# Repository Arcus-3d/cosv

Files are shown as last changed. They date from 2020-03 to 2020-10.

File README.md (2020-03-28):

## COSV - Cam Open Source Ventilator.
Cam based ventilator designed to fit directly on an BVM, on the patient.
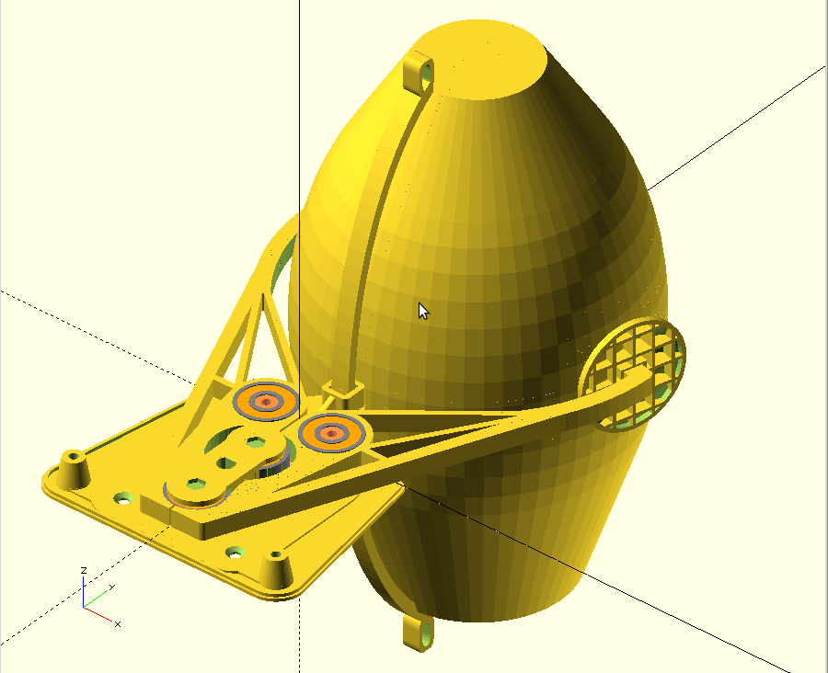
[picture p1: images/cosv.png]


The [COSV - Cam Open Source Ventilator](https://hackaday.io/project/170507) project is open source hardware. 
This github repository hosts the [OpenSCAD](http://www.openscad.org) source and the rendered STL images for quick access.

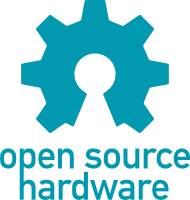
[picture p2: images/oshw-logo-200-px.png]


Hardware designs (schematics and CAD) files are licensed under the [Creative Commons Attribution-ShareAlike 3.0 Unported License](http://creativecommons.org/licenses/by-sa/3.0/) and follow the terms of the [OSHW (Open-source hardware) Statement of Principles 1.0.](http://freedomdefined.org/OSHW)

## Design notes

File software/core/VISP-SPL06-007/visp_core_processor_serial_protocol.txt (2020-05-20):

VISP Core Processor Serial Data Format

Note: <t> is time on the core,based on milliseconds since power up.

Sensor Readings
d,<t>,<pressure cmH20>,<smoothed volume (mL)>,<tidal volume (mL)>[,<s1>,<s2>,<s3>,<s4>] (UNSOLICITED)

Logging Output (UNSOLICITED)
i,<t>,<informational string>
g,<t>,<debug string>
w,<t>,<warning string>
c,<t>,<critical string>

Health Status Reports have the text "good" or "bad" based on the active status of the core. (can be UNSOLICITED)
H

Core responds with timestamp and status string.
H,<t>,[good|bad]

Calibrate now
C
Core responds with timestamp, status code, and status string.
C,<t>,<status>,<string>

Example responses:
C,<t>,0,Starting
C,<t>,1,In Progress
C,<t>,2,Complete

Reboot command.   Reboots the core
R
Core does not respond to a Reboot command

Identification Command (UNSOLICITED RESPONSE HAPPENS AT STARTUP)
I
Core responds with
I,<t>,<string>,<major>,<minor>,<revision>

EEPROM read/write
An empty parameter string makes the core echo back all 128 bytes of EEPROM data.
Providing the address will reply with a full page (16-bytes) starting at that address,
Providing the address and data will write the data to the EEPROM, on write
to byte 127, the EEPROM data will be committed to the EEPROM.
E
E,<address>
E,<address>,<b_0>

Response will always consist of a time, address, and data bytes
E,<t>,<address>,<b0>,<b1>,<b2>...

Settings.  There are many settings available, use 'Q' to query them all
S
Core replies with all settings (no limits or dictionaries)

Example S output
S,176825,mode,value,PC-CMV
S,176825,rate,value,5
S,176826,ie,value,1:2
S,176826,volume,value,0
S,176828,pressure,value,0
S,176830,breathThreshold,value,0
S,176833,bodytype,value,Venturi
S,176836,calib0,value,-38256.90
S,176838,calib1,value,-38303.29
S,176841,calib2,value,-37957.33
S,176844,calib3,value,114517.55
S,176847,sensor0,value,BMP280
S,176849,sensor1,value,BMP280
S,176852,sensor2,value,BMP388
S,176855,sensor3,value,BMP388
S,176858,motorType,value,Unknown
S,176861,motorSpeed,value,0
S,176863,motorMinSpeed,value,60
S,176866,motorHomingSpeed,value,0
S,176869,motorStepsPerRev,value,200
S,176872,debug,value,Disable

Settings Query 1 setting command
S,mode
Core replies with the current "mode" setting
S,<t>,mode,Unknown

Settings set command
S,mode,PC-CMV
Core replies with the current setting with a list of *_display Enabled/Disabled for the settings relavent to this mode
S,<t>,mode,PC-CMV

Example "S,mode,PC-CMV" output
S,140581,mode,value,PC-CMV
S,140581,mode,enabled,True
S,140582,rate,enabled,True
S,140583,ie,enabled,True
S,140585,volume,enabled,False
S,140588,pressure,enabled,True
S,140591,breathThreshold,enabled,False
S,140594,bodytype,enabled,False
S,140597,calib0,enabled,False
S,140600,calib1,enabled,False
S,140602,calib2,enabled,False
S,140605,calib3,enabled,False
S,140607,sensor0,enabled,False
S,140610,sensor1,enabled,False
S,140613,sensor2,enabled,False
S,140615,sensor3,enabled,False
S,140618,motorType,enabled,True
S,140621,motorSpeed,enabled,True
S,140624,motorMinSpeed,enabled,True
S,140627,motorHomingSpeed,enabled,True
S,140631,motorStepsPerRev,enabled,True
S,140634,debug,enabled,True

mode sets the operational mode using "PC-CMV" or "VC-CMV)
rate controls the rate in which the breath is delivered
volume controls the volume in mL of breaths (tidal volume)
pressure controls the pressure used in PC-CMV
ie is the inhale:exhale ratio
breathInterval controls the time period between breaths in milliseconds. (Continuous Mandatory Ventilation)
debug enable or disable the internal debugging output
motorSpeed Internal testing, turns motor on at a specific speed
bodytype Switches the algorithm used for the core
calib0-3 Current calibration settings for each sensor
sensor0-3 Current sensor detected.  Sensor0=U5, Sensor1=U6, Sensor2=U7, Sensor3=U8
motorType Used to set the type of motor attached 
motorSpeed Used to set the current speed of the motor
motorMinSpeed Minimum speed for the motor to use for initial starting of a breath cycle
motorHomingSpeed Homing speed of the motor
motorStepsPerRev For steppers, how many steps per rev (200, 400, etc)

Query all settings.  This a display will want to do on startup, to determine the capabilities of the core.
Q
The Core will respond with 'H', and 'S' responses for all settings and limits/dictionaries.

Example Q output
S,2394,mode,dict,OFF,Offline,PC-CMV,Pressure Controlled CMV,VC-CMV,Volume Controlled CMV
S,2397,mode,group,button
S,2399,mode,enabled,True
S,2401,mode,value,OFF
S,2403,rate,min,5
S,2405,rate,max,20
S,2406,rate,group,button
S,2409,rate,enabled,True
S,2411,rate,value,5
S,2413,ie,dict,1:2,50% duty cycle,1:3,33% duty cycle,1:4,25% duty cycle,1:5,20% duty cycle
S,2420,ie,group,button
S,2422,ie,enabled,True
S,2424,ie,value,1:2
S,2426,volume,min,0
S,2428,volume,max,1000
S,2430,volume,group,button
S,2433,volume,units,mL
S,2435,volume,enabled,True
S,2437,volume,value,0
S,2439,pressure,min,0
S,2441,pressure,max,100
S,2443,pressure,group,button
S,2446,pressure,units,cmH2O
S,2448,pressure,enabled,True
S,2451,pressure,value,0
S,2453,breathThreshold,min,0
S,2455,breathThreshold,max,1000
S,2458,breathThreshold,group,button
S,2461,breathThreshold,enabled,False
S,2464,breathThreshold,value,0
S,2467,bodytype,dict,Unknown,Unknown,Pitot,Pitot body style,Venturi,Venturi body style
S,2475,bodytype,group,button
S,2478,bodytype,enabled,False
S,2480,bodytype,value,Venturi
S,2483,calib0,min,-1000
S,2485,calib0,max,1000
S,2487,calib0,group,status
S,2489,calib0,units,pascals
S,2491,calib0,enabled,False
S,2494,calib0,value,5035907.00
S,2497,calib1,min,-1000
S,2499,calib1,max,1000
S,2501,calib1,group,status
S,2503,calib1,units,pascals
S,2505,calib1,enabled,False
S,2508,calib1,value,5038159.00
S,2510,calib2,min,-1000
S,2512,calib2,max,1000
S,2514,calib2,group,status
S,2518,calib2,units,pascals
S,2520,calib2,enabled,False
S,2523,calib2,value,5021042.50
S,2525,calib3,min,-1000
S,2527,calib3,max,1000
S,2529,calib3,group,status
S,2532,calib3,units,pascals
S,2534,calib3,enabled,False
S,2536,calib3,value,-2525668.30
S,2539,sensor0,dict,Unknown,Unknown,BMP388,BMP388,BMP280,BMP280,SPL06,SPL06
S,2546,sensor0,group,status
S,2548,sensor0,enabled,False
S,2550,sensor0,value,BMP280
S,2553,sensor1,dict,Unknown,Unknown,BMP388,BMP388,BMP280,BMP280,SPL06,SPL06
S,2560,sensor1,group,status
S,2563,sensor1,enabled,False
S,2565,sensor1,value,BMP280
S,2568,sensor2,dict,Unknown,Unknown,BMP388,BMP388,BMP280,BMP280,SPL06,SPL06
S,2574,sensor2,group,status
S,2576,sensor2,enabled,False
S,2579,sensor2,value,BMP388
S,2581,sensor3,dict,Unknown,Unknown,BMP388,BMP388,BMP280,BMP280,SPL06,SPL06
S,2588,sensor3,group,status
S,2590,sensor3,enabled,False
S,2593,sensor3,value,BMP388
S,2595,motorType,dict,Unknown,Unknown,AutoDetect,Start Motor Autodetection,BLDC,BLDC,Stepper,Stepper,Wiper,Wiper
S,2605,motorType,group,button
S,2608,motorType,enabled,True
S,2611,motorType,value,Unknown
S,2613,motorSpeed,min,0
S,2615,motorSpeed,max,100
S,2618,motorSpeed,group,button
S,2620,motorSpeed,units,%
S,2622,motorSpeed,enabled,True
S,2625,motorSpeed,value,0
S,2627,motorMinSpeed,min,0
S,2630,motorMinSpeed,max,100
S,2632,motorMinSpeed,group,button
S,2635,motorMinSpeed,units,%
S,2638,motorMinSpeed,enabled,True
S,2640,motorMinSpeed,value,60
S,2643,motorHomingSpeed,min,0
S,2647,motorHomingSpeed,max,100
S,2649,motorHomingSpeed,group,button
S,2653,motorHomingSpeed,units,%
S,2655,motorHomingSpeed,enabled,True
S,2658,motorHomingSpeed,value,0
S,2661,motorStepsPerRev,min,0
S,2664,motorStepsPerRev,max,1600
S,2667,motorStepsPerRev,group,button
S,2670,motorStepsPerRev,enabled,True
S,2673,motorStepsPerRev,value,200
S,2676,debug,dict,Disable,Disabled,Enable,Enabled
S,2680,debug,group,button
S,2682,debug,enabled,True
S,2684,debug,value,Disable
Q,2688,Finished

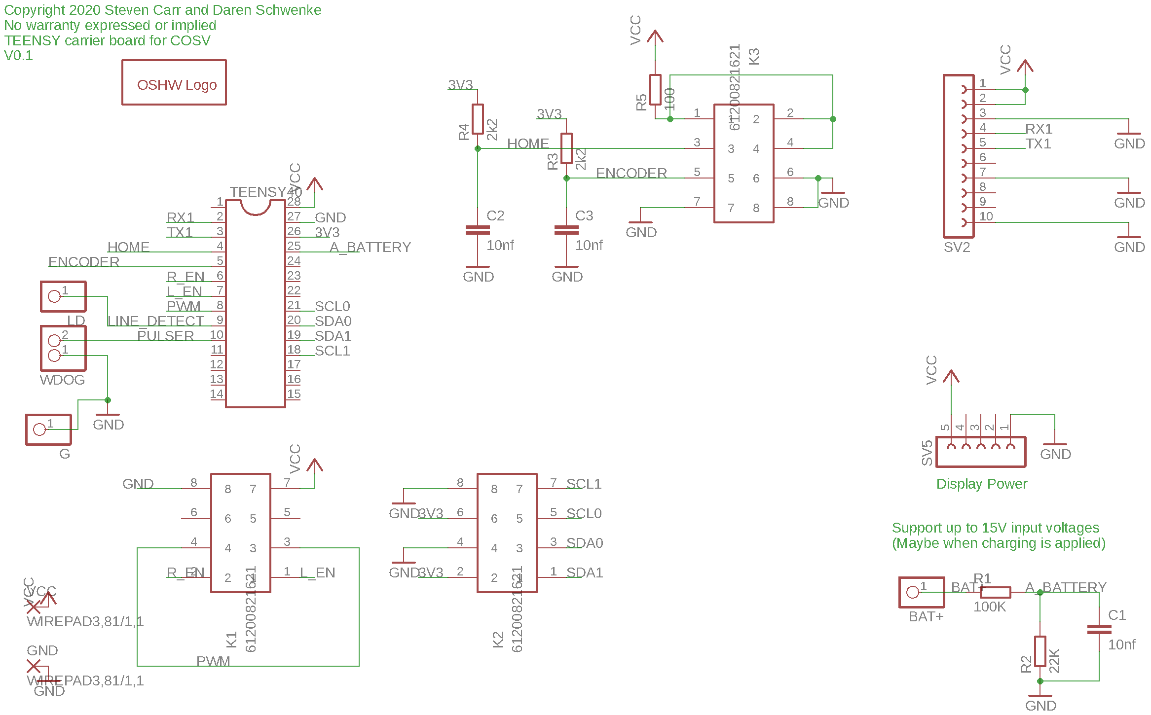
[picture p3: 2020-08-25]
pcb/COSV-PCB/Carrier-TEESNSY40/cosv-carrier-teensy4-schematic.png

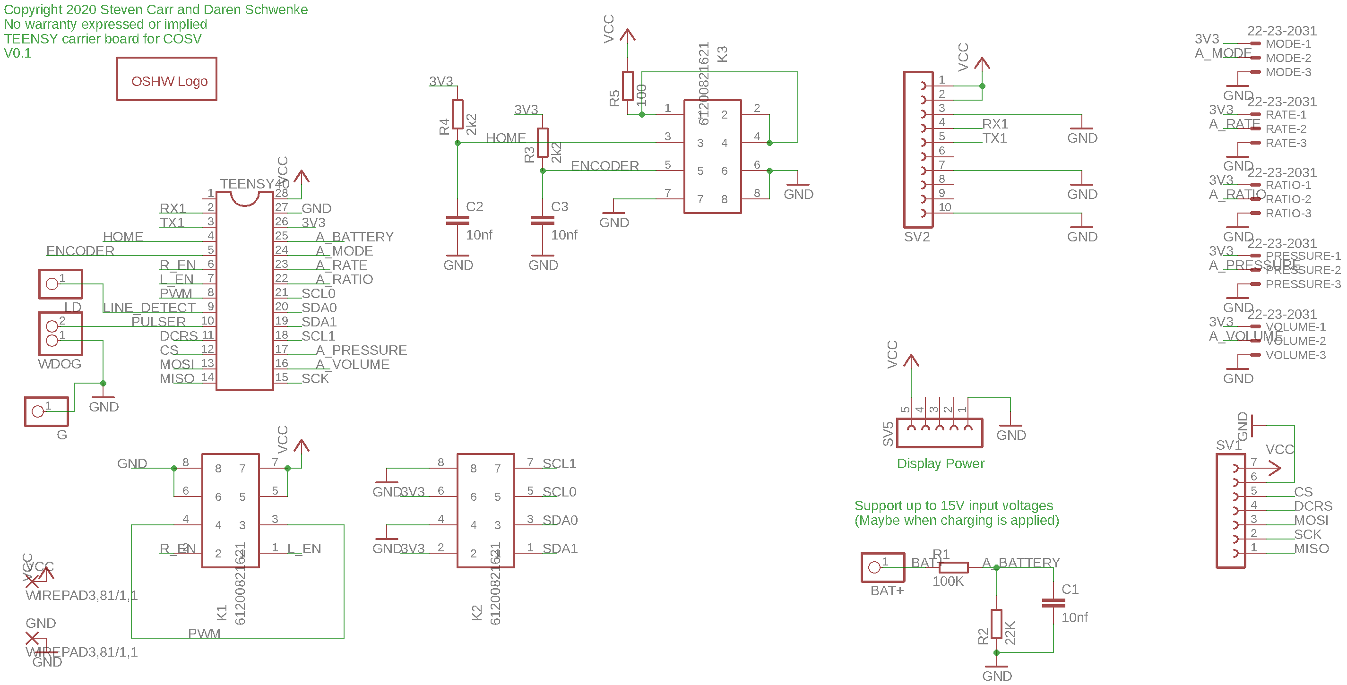
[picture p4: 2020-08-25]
pcb/COSV-PCB/Carrier-TEESNSY40-PlusAnalog/cosv-carrier-teensy4-schematic.png

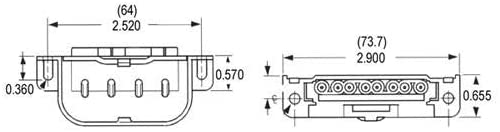
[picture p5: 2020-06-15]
images/2G11_socket.jpg

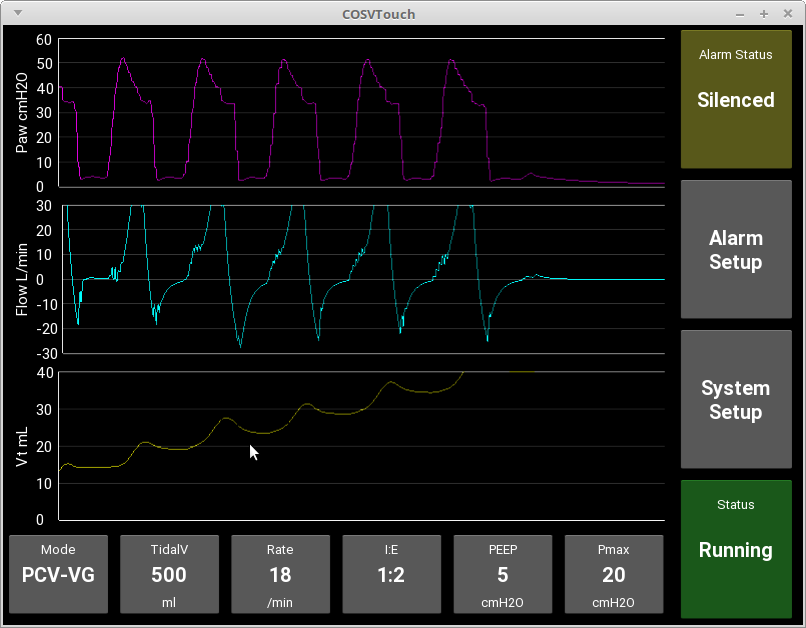
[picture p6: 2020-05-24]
images/rising_graph.png

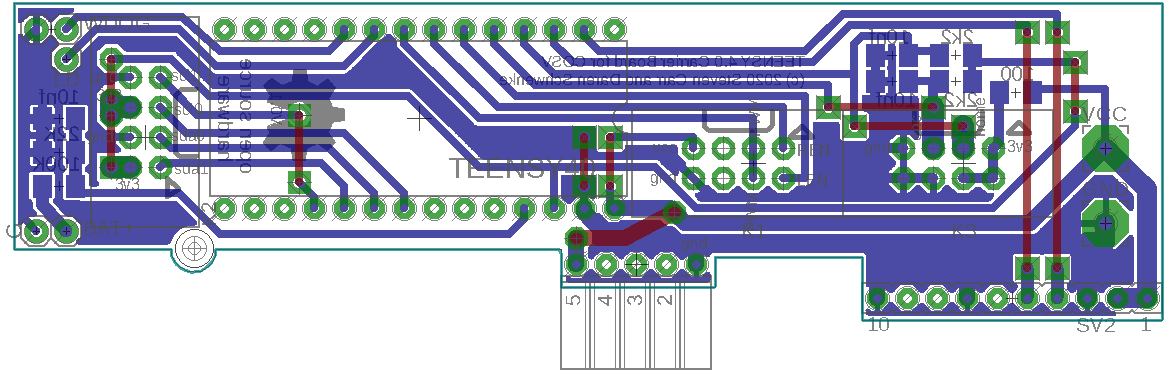
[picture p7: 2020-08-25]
pcb/COSV-PCB/Carrier-TEESNSY40/cosv-carrier-teensy4-board.png

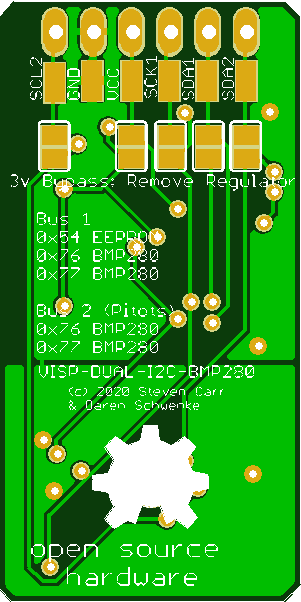
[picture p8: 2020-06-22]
pcb/VISP-PCB/VISP-I2C-DUAL/pcbbot.png

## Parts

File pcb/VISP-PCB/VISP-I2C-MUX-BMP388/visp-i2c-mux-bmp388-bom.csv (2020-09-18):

Item # | Qty | Ref Des | Manufacturer | Mfg Part # | Dist. Part # | Description | Package | Type
1 | 2 | C1,C3 | Murata Electronics | GRM188R61A106KE69J | 490-14372-1-ND | 10uF ceramic capacitor | 0805 | SMT
2 | 6 | C2,C4,C5,C6,C7,C9 | Murata Electronics | GRM155R71C104KA88J | 490-6328-1-ND | 100nF ceramic capacitor | 0402 | SMT
3 | 8 | R1,R2,R8,R9,R10,R11,R22,R23 | TE Connectivity Passive Product | CRGCQ0402F2K7 | A129632CT-ND | 2k7 resistor | 0402 | SMT
4 | 4 | R3,R5,R6,R7 | TE Connectivity Passive Product | CRGCQ0402J10K | A130054CT-ND | 10K resistor | 0402 | SMT
5 | 1 | R4 | TE Connectivity Passive Product | CRGCQ0402F47R | A129611CT-ND | 47 ohm resistor | 0402 | SMT
6 | 1 | LED1 | Rohm Semiconductor | SML-D12P8WT86 | 511-1579-1-ND | LED GREEN DIFFUSED 0603 SMD | 0603 | SMT
7 | 1 | U1 | Microchip Technology | MIC5225-3.3YM5-TR | 576-2980-1-ND | IC REG LINEAR 3.3V 150MA SOT23-5 | SOT23-5 | SMT
8 | 1 | U2 | Texas Instruments | TCA9546APWR | 296-40578-1-ND | IC I2C SW 4CH W/RESET 16TSSOP | 16TSSOP | SMT
9 | 1 | U3 | Microchip Technology | AT24C512C-SSHD-T | AT24C512C-SSHD-TCT-ND | IC EEPROM 512K I2C 1MHZ 8SOIC | SO-08M | SMT
10 | 4 | U5,U6,U7,U8 | Bosch Sensortec | BMP388 | 828-1079-1-ND | Barometric Pressure Sensor | BMP388 | SMT
Unique | 10
Total | 29
Thru Hole | 0
Has BGA | Yes

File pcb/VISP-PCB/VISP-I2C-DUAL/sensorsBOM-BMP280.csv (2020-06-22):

Qty | Designator | Footprint | Comment | LCSC Part # (optional) | Description (optional)
2 | C1,C3 | C0805 | 10uF ±10% 10V | C15850 | 10uF ±10% 10V B 0805 Multilayer Ceramic Capacitors MLCC - SMD/SMT RoHS
5 | C4,C5,C6,C7,C9 | C0402 | 100nF ±10% 50V X7R | C1525
4 | Q1,Q2,Q3,Q4 | SOT-23-3 | BSS138 | C78284 | N Channel 50V 220mA 1.5V @ 1mA 3.5 Ω @ 220mA,10V 360mW SOT-23(SOT-23-3) MOSFET RoHS
8 | R1,R2,R3,R5,R6,R7,R8,R9 | R0402 | 10K ±1% 1/16W | C25744 | 10K ±1% 1/16W 0402 Chip Resistor - Surface Mount RoHS
1 | R4 | R0402 | 47K ±1% 1/16W | C25792 | 47K ±1% 1/16W 0402 Chip Resistor - Surface Mount RoHS
1 | LED1 | LED_0603 | Light Emitting Diodes (LED) Green 520~535nm 112~258mcd@20mA | C72043 | Light Emitting Diodes (LED) Green 520~535nm 112~258mcd@20mA
1 | U1 | SOT-23-5 | BL9198-33BAPRN | C51282 | Fixed 6V 3.3V 300mA SOT-23-5 Low Dropout Regulators(LDO) RoHS
1 | U3 | SO-8 | M24C01-RMN6TP | C146163 | SO-8 EEPROM RoHS
4 | U5,U6,U7,U8 | LGA-8 | BMP280 | C83291 | LGA-8 Gas Sensors RoHS

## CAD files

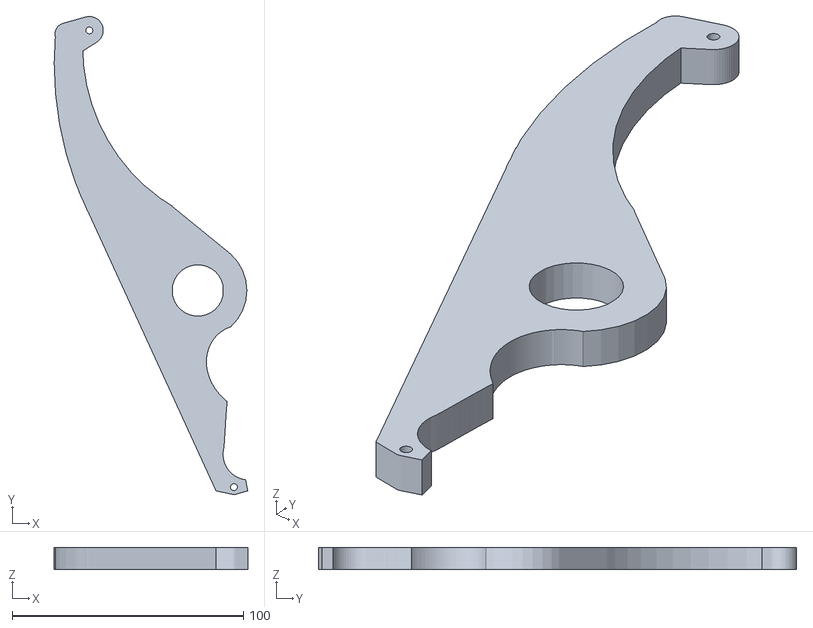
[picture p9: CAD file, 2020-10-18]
hardware/rendered/FFF/arm.stl
83.7 x 206.6 x 9.54

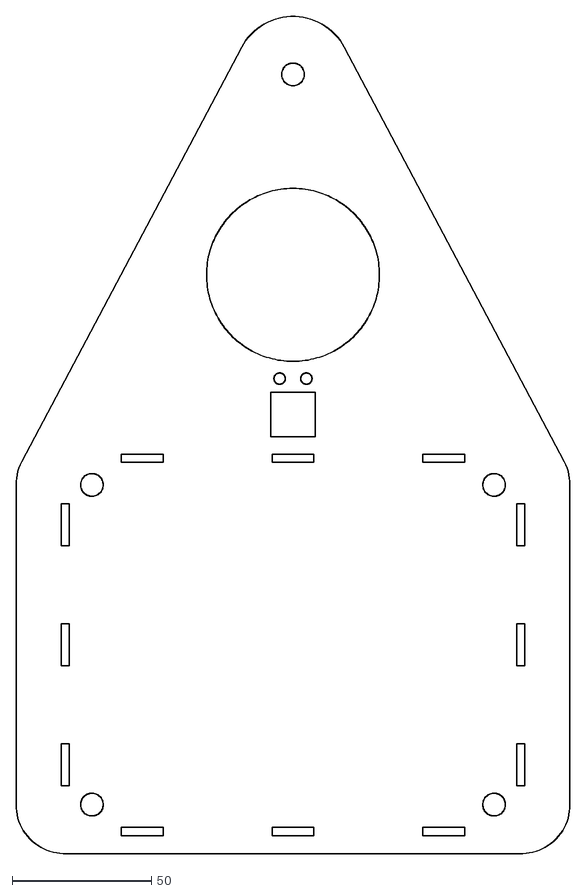
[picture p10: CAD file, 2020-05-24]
hardware/rendered/Laser/kerf_0.04_mat_3.0/laser_base_end_right_inner.dxf
198.6 x 300.2

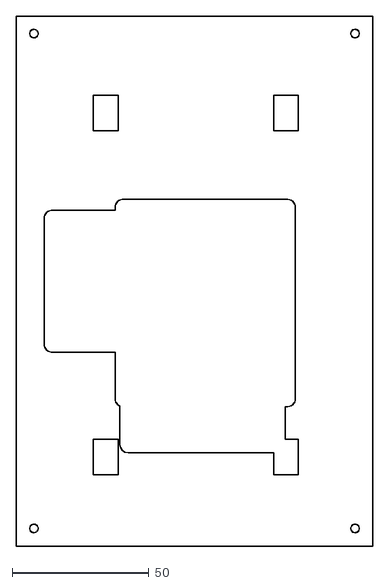
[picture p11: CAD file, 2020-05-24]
hardware/rendered/Laser/kerf_0.15_mat_3.0/laser_base_front_pi_layer_0.dxf
130.4 x 194.0

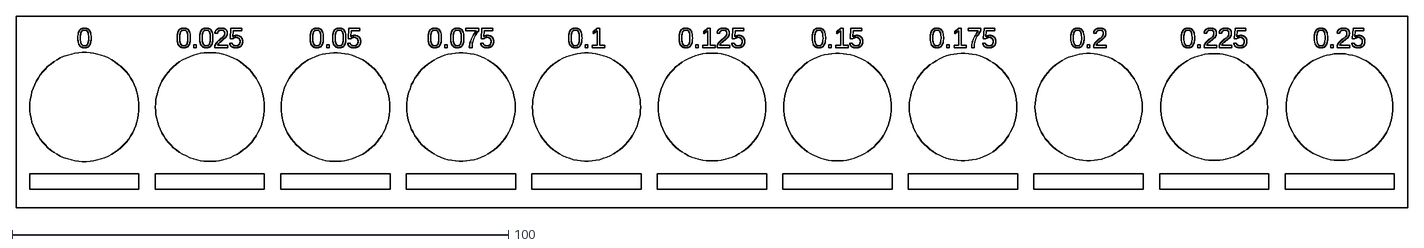
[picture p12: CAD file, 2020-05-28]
hardware/rendered/Laser/kerf_slot_test.dxf
280.5 x 38.5

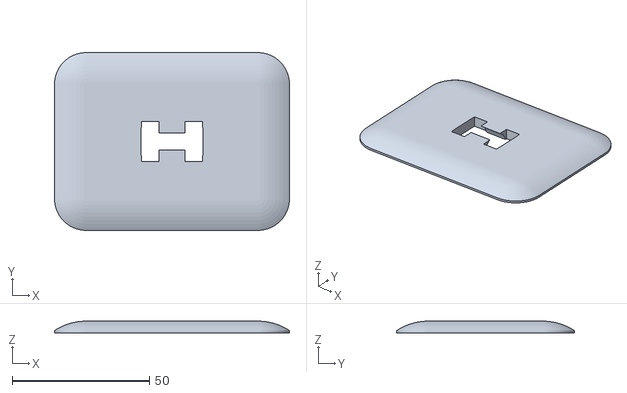
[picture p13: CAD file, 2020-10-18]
hardware/rendered/FFF/paddle.stl
85.5 x 64.6 x 4.28

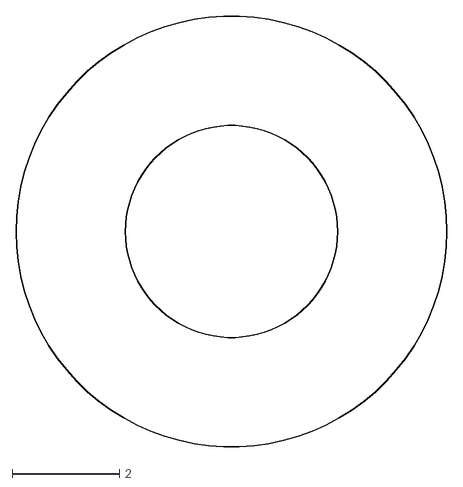
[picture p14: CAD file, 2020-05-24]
hardware/rendered/Laser/kerf_0.04_mat_3.0/laser_bearing_bushing_4x8mm.dxf
8.04 x 8.04

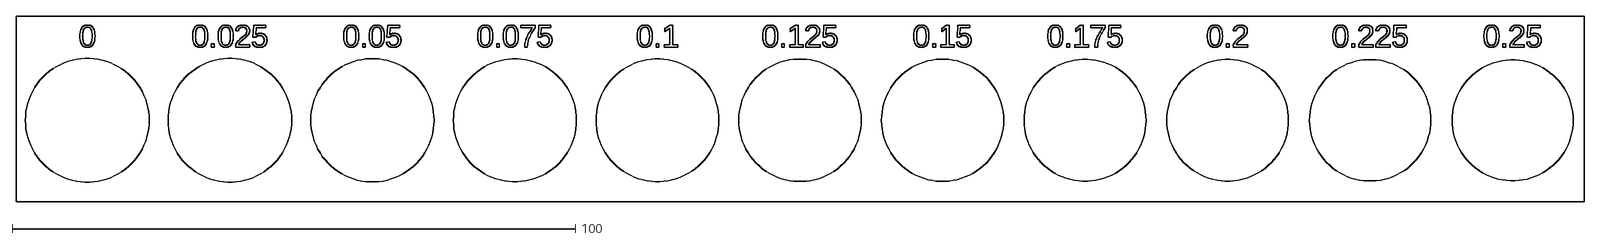
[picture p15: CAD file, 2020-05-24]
hardware/rendered/Laser/kerf_0.15_mat_3.0/laser_bearing_kerf_test.dxf
278.3 x 33.0

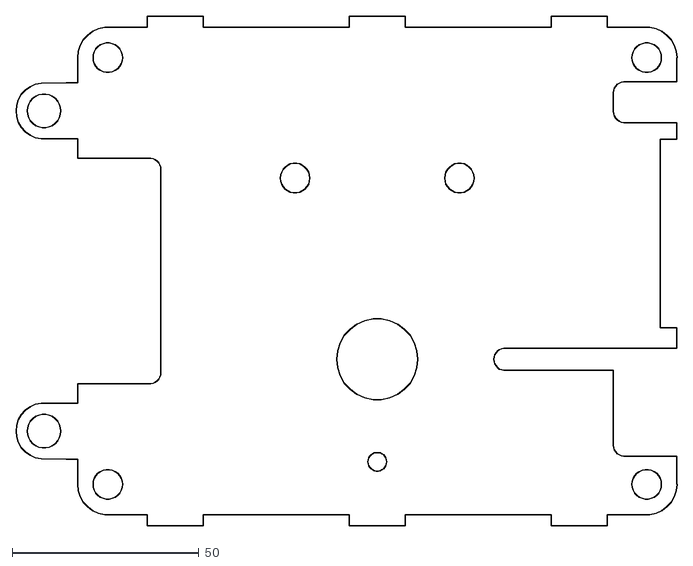
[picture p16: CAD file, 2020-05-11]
hardware/rendered/Laser/laser_base_mount_top.dxf
176.9 x 136.4

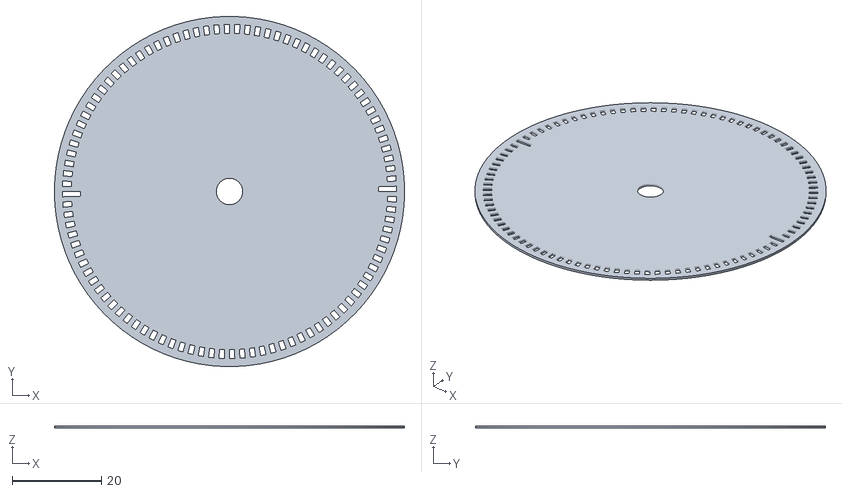
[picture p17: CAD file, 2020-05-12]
hardware/rendered/FFF/cam_encoder.stl
78.5 x 78.5 x 0.5

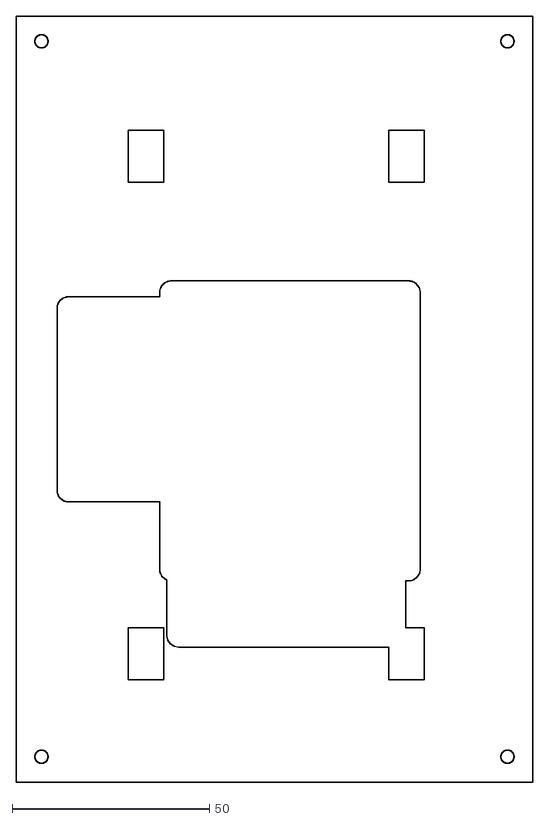
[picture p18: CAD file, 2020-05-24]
hardware/rendered/Laser/kerf_0.04_mat_3.0/laser_base_front_pi_layer_0.dxf
130.9 x 194.0

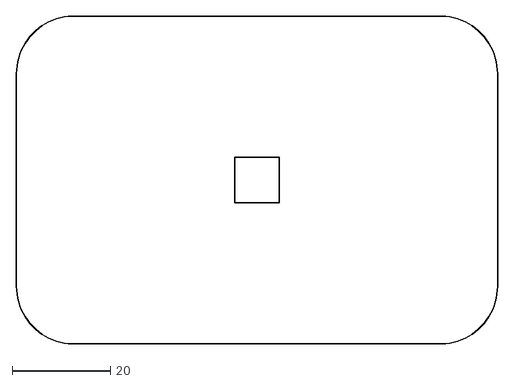
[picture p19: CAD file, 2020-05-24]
hardware/rendered/Laser/kerf_0.15_mat_3.0/laser_paddle_layer_0.dxf
98.1 x 66.9

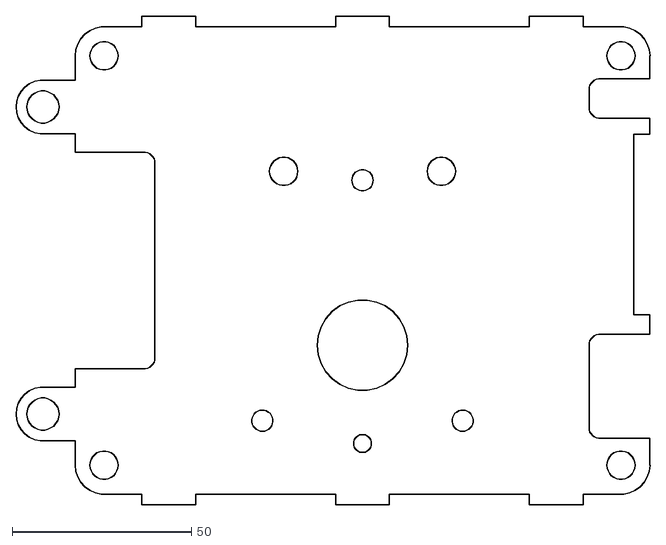
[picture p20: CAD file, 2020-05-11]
hardware/rendered/Laser/laser_base_mount_bottom.dxf
176.9 x 136.4

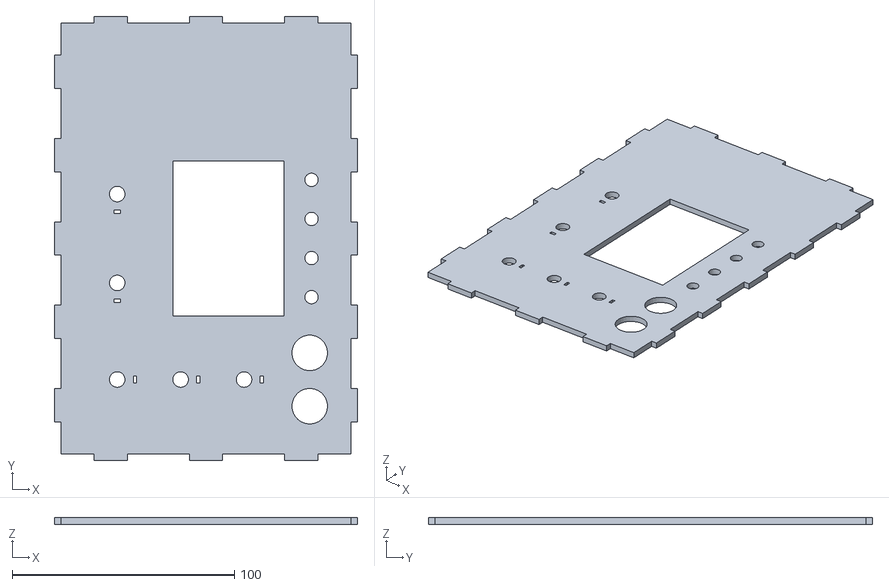
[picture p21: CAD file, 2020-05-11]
hardware/rendered/FFF/base_front.stl
136.4 x 200.0 x 3.00

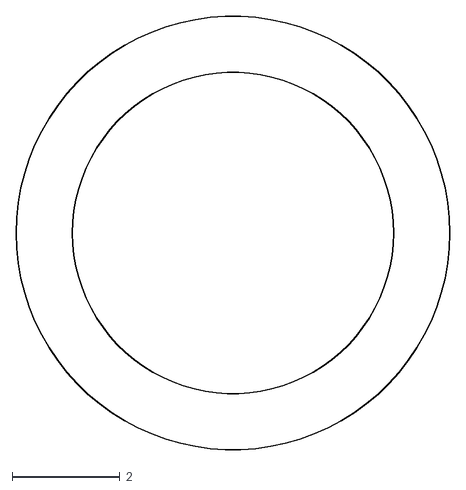
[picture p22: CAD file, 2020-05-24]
hardware/rendered/Laser/kerf_0.04_mat_3.0/laser_bearing_bushing_6x8mm.dxf
8.04 x 8.04

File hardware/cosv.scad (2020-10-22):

/*	Project name:		COSV - Cam Open Source Ventilator
	Project home: 		https://hackaday.io/project/170507
	Project repo: 		https://github.com/Arcus-3d/cosv
	Project authors: 	Daren Schwenke, Steven Carr

	Software license: 	http://www.gnu.org/licenses/gpl-3.0.html
	Hardware license: 	https://ohwr.org/cern_ohl_s_v2.txt
	Hardware note: 		Defensive patents for the relevant novel hardware elements of this project have been filed.  
				Kindly follow our Open Source Hardware licensing requirements. Thank you.
	Project version: 	0.20
	Version note: 		The *vast* majority of files which have been recently generated target equal height/multiple millimeter based layer construction.
				In other words, if you are not laser cutting this from sheet stock around 3mm thick for all but paddle() and flow_sensor_venturi_for_pcb()
				you may have issues.
 				There are *very* likely artifacts for the FFF and milled version of the files you can generate.
 				Please do a little sanity check if you generate your own FFF or milled files please.  
				If you are looking at a rendered file in the repository, it should be the latest version.	
	Abbreviations:
				r=radius (and sometimes rotation within modules)
				ir=inner radius
				or=outer radius
				t=thickness
				l=length
				h=height
				w=width
				d=depth
				x,y,z=dimensions in x,y,z
*/



/* [Global] */

/* [COSV Customization] */
// Circle complexity: Turn down to about 30 for working, up to like 90 for rendering
param_complexity=15; // [1:100]

// Generates the path for the cam.  The cam surface is generated by subtraction of the cam bearing from the surface while rotating both the cam and the arms.  This is the angle to rotate between steps when generating this. Smaller values result in smoother, but more complicated surfaces.  A good value for working is 15. A good value for rendering is 2-5.
param_path_step=15; // [1:15]

// Line width for laser cutting.  Affects hole sizes
//param_kerf=0.15; // [0.000:0.005:0.500]
param_kerf=0.00; // [0.000:0.005:0.500]

// Motor mount selection
param_motor="wiper"; // [wiper:Ford F150 Wiper Motor,bldc:BLDC Brushless Motor,worm:Worm gear motor,nema23:Nema23 Stepper with 6mm shaft,nema23-635:Nema23 Stepper with 6.35mm shaft]

// Is the motor shaft D-Shaped?
param_d_shaft = "auto"; // [zero:Circular,one:D-Shaped,two:Double-D shaped (wiper motor),auto:D or DD based on motor type]

// Which one would you like to see?
param_part = ""; // REPLACE_ME_PART_TRAP_EM_ECALPER 

/* [Hidden] */


// Don't touch $fn, the param_complexity variable is over-ridden in the makefile
$fn=param_complexity;


// Generates the path for the cam.  The cam surface is generated by subtraction of the cam bearing from the surface
// while rotating both the cam and the arms.  This is the angle to rotate between steps when generating this.
// Smaller values result in smoother, but more complicated surfaces.  
// A good value for working is 15. A good value for rendering is 1.
path_step=param_path_step; // [1:15]

PART=param_part;


//////////////////////////////////////////////////////////////////
// Assembly views, for testing
rotate([90,0,0]) cosv_assembly_view(cam_angle=$t*180,explode=0);
//base_handle();
//cam_assembly_view(explode=0);
//flow_sensor_assembly_view(rot=360*$t,explode=0.1);

//////////////////////////////////////////////////////////////////
// Laser parts, for testing

//laser_base_mount_left(); // GROUP Laser DESC "cam/arm mount opposite motor" 
//laser_base_mount_right(); // GROUP Laser DESC "cam/arm mount motor side"

//laser_arm(path_step=1,$fn=90); // GROUP Laser DESC  "arm for the bag" NAME="laser_arm" QTY 6
//laser_arm_end_support(); // GROUP Laser DESC "small support triangles for the paddle from the arm" QTY 16

//laser_base_end_right(slots=0,battery=0); // GROUP Laser DESC "outer end plate with bvm_br sized bag hole" NAME="laser_base_end_right"
//laser_base_end_left(slots=0,battery=0); // GROUP Laser DESC "outer end plate with bvm_tr sized bag hole" NAME="laser_base_end_left"

//laser_base_end_right(slots=1,battery=0); // GROUP Laser DESC  "inner end plate with bvm_br sized bag hole" NAME="laser_base_end_right_with_slots"
//laser_base_end_left(slots=1,battery=1); // GROUP Laser DESC "inner end plate with bvm_tr sized bag hole" NAME="laser_base_end_left_with_slots"

//laser_base_battery_mount_t(); // GROUP Laser DESC  "battery mounts"
//laser_base_battery_mount_b(); // GROUP Laser DESC  "battery mounts"

//laser_arm_mount(motor=1); //  GROUP Laser DESC "bushings from cam/arm mount to the arm bearings, with a hole for the motor mount" NAME="laser_arm_motor_mount" QTY 3
//laser_arm_mount(motor=0); //  GROUP Laser DESC "bushings from cam/arm mount to the arm bearings" NAME="laser_arm_mount" QTY 3

//laser_base_front_analog(); //  GROUP Laser DESC "front panel for analog controls and small SPI display"
//laser_base_front_pi(layer=0); // GROUP Laser DESC "front panel for pi touchscreen.  Three layers required." NAME="laser_base_front_pi_0"
//laser_base_front_pi(layer=1); // GROUP Laser DESC "front panel for pi touchscreen.  Three layers required." NAME="laser_base_front_pi_1"
//laser_base_front_pi(layer=2); // GROUP Laser DESC "front panel for pi touchscreen.  Three layers required." NAME="laser_base_front_pi_2"

//laser_base_front(); // GROUP Laser DESC "base front inner panel"
//laser_base_back(); // GROUP Laser DESC "base back inner panel"
//laser_base_back_wiper(); // GROUP Laser DESC "base back panel for wiper motor, h-bridge, switch, and power plug"

//laser_cam_end_plate_b(); // GROUP Laser DESC "cam end plate motor side" NAME="laser_cam_end_plate_wiper_6mm" QTY 2
//laser_cam_end_plate_t(); // GROUP Laser DESC "cam end plate opposite motor" NAME="laser_cam_end_plate_wiper_double_d" QTY 2

//laser_cam_center_b(); // GROUP Laser DESC "cam center with motor shaft cutout"
//laser_cam_center_t(); // GROUP Laser DESC "cam center with motor shaft bolt cutout"
//laser_bearing_kerf_test(); // GROUP Test DESC "Laser bearing kerf test"
//laser_cam_encoder(); // GROUP Laser DESC "cam end with encoder slots for optical gate"

//laser_base_top(); // GROUP Laser DESC "top panel with rj45 jack and holes for arms"
//laser_base_bottom(); // GROUP Laser DESC "bottom panel"

//laser_bearing_bushing(ir=4/2,or=8/2); // GROUP Laser DESC "bushing for cam bearings" NAME="laser_bearing_bushing_4x8mm" QTY 6
//laser_bearing_bushing(ir=6/2,or=8/2); // GROUP Laser DESC "bushing for motor shaft bearing" NAME="laser_bearing_bushing_6x8mm" QTY 3

//laser_paddle(layer=0,h=material_t*3); // GROUP Laser DESC "paddles for the arms." NAME="laser_paddle_0" QTY 4
//laser_paddle(layer=1,h=material_t*3); // GROUP Laser DESC "paddles for the arms." NAME="laser_paddle_1" QTY 2

//laser_nut_support(); // GROUP Laser DESC "little glue-on nut holder to eliminate a whole layer otherwise" QTY 8

//////////////////////////////////////////////////////////////////
// FFF parts, for testing.  May be out of date!

//flow_sensor_pitot_for_pcb(); // GROUP VISP DESC "Flow Sensor Pitot Style"
//flow_sensor_venturi_for_pcb(); //  GROUP VISP DESC "Flow Sensor Venturi Style"
//flow_sensor_cover(oled=0); //  GROUP VISP DESC "Flow Sensor Cover With OLED" NAME "flow_sensor_cover_oled"
//flow_sensor_cover(); // GROUP VISP DESC "Flow Sensor Cover"

//cam(); // cam top/bottom.
//cam_encoder(h=0.5);

//paddle(); // paddle for the arms.

//arm();

//base_mount_left();
//base_mount_right();

//base_end_left(battery=1); 
//base_end_right(); 

//base_front();
//base_front_analog();
//base_front_pi(layer=1);

//base_battery_mount_t();
//base_battery_mount_b();
//base_back();
//base_back_wiper();

//base_top();
//base_bottom();

//bearing_bushing();
//bearing_washer();

//supply_cover();
//bldc_motor_standoff(); // bldc motor has a long pilot on it, which requires a standoff

//translate([0,0,material_t]) rotate([0,90,0]) arm_end_lock(); // in progress

//////////////////////////////////////////////////////////////////
// Part models, for testing
//optical_gate();
//base_plate(); // top plate/electronics mount.  Need 1.
//flow_sensor_test();

// Clearance for parts, and extra length to make subtractions clean.
clearance=0.4;
extra=0.02;

// nozzle size for 3D printing.  Generates parts that are exactly a multiple of this width for strength
nozzle_r=0.4/2;

// line width for laser cutting.  Affects hole sizes (param_kerf is CLI overridden by Makefile)
kerf=param_kerf;

// material thickness for laser cutting
material_t=3.175;

battery_x=153;
battery_terminal_y=6;
battery_y=95.5;
battery_z=65.5;

arm_w=12*nozzle_r*2; 
arm_h=material_t*3;
bearing_or=22/2-kerf;
bearing_ir=8/2+kerf;
bearing_h=7;

// bag dimensions and position
bvm_r=125/2;
bvm_br=63/2;
bvm_tr=42/2;
bvm_l=200;
bvm_c=nozzle_r*2*8; // Thickness for bag parts
bvm_y_offset=30; // Moves the bag location up/down
bvm_y_center=bvm_r+bearing_or/2+bvm_y_offset+arm_w*2;

// a little washer to clearance the bearing
bearing_washer_h=(arm_h-bearing_h)/2;
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

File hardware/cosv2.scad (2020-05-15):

// Project name:		COSV - Cam Open Source Ventilator
// Project home: 		https://hackaday.io/project/170507
// Project repository: 		https://github.com/Arcus-3d/cosv
// Project authors: 		Daren Schwenke, Steven Carr

// Hardware license: 		https://ohwr.org/cern_ohl_s_v2.txt
// Software license: 		http://www.gnu.org/licenses/gpl-3.0.html
// Hardware license note: 	Defensive patents for the relevant novel hardware elements of this project have been filed.  
//				Kindly follow our Open Source Hardware licensing requirements, or we do have the legal right to spank you.
//				Thank you.

// Project version: 		0.19
// Version note: 		The *vast* majority of files which have been recently generated target equal height/multiple millimeter based layer construction.
//				In other words, if you are not laser cutting this from sheet stock around 3mm thick for all but paddle() and flow_sensor_venturi_for_pcb()
//				you may have issues.
// 				There are *very* likely artifacts for the FFF and milled version of the files you can generate.
// 				Please do a little sanity check if you generate your own FFF or milled files please.  
//				If you are looking at a rendered file in the repository, it should be the latest version.	

/* [Global] */

/* [COSV Customization] */
// Circle complexity: Turn down to about 30 for working, up to like 90 for rendering
param_complexity=30; // [1:100]

// Generates the path for the cam.  The cam surface is generated by subtraction of the cam bearing from the surface while rotating both the cam and the arms.  This is the angle to rotate between steps when generating this. Smaller values result in smoother, but more complicated surfaces.  A good value for working is 15. A good value for rendering is 2-5.
param_path_step=15; // [1:15]

// Line width for laser cutting.  Affects hole sizes
param_kerf=0.15; // [0.000:0.005:0.500]

// Motor mount selection
param_motor="wiper"; // [wiper:Ford F150 Wiper Motor,bldc:BLDC Brushless Motor,worm:Worm gear motor,nema23:Nema23 Stepper with 6mm shaft,nema23-635:Nema23 Stepper with 6.35mm shaft]

// Is the motor shaft D-Shaped?
param_d_shaft = "auto"; // [zero:Circular,one:D-Shaped,two:Double-D shaped (wiper motor),auto:D or DD based on motor type]

// Which one would you like to see?
param_part = ""; // [cam:cam top/bottom - need 2,paddle:paddle for the arms - need 2,base_mount_right:base plate/motor mount - need 1,base_mount_left:top plate/electronics mount - need 1,bldc_motor_standoff:bldc motor standoff - need 1,arm:Arm,supply_cover:Power Supply cover,chest_bar:Chest bar,flow_sensor_pitot_for_pcb:Flow sensor body for use with a PCB (pitot style),flow_sensor_venturi_for_pcb:Flow sensor body for use with a PCB (venturi style),flow_sensor_cover_oled:Flow sensor cover for use with embedded OLED,flow_sensor_cover:Flow sensor cover,flow_sensor_test:Test apparatus for the flow sensor,bearing_bushing:bearing_busing - used within the other FFF parts,bearing_washer:bearing_washer - used within the other FFF parts,laser_callibration_square_10x10mm:Laser calibration square - A 10x10mm square in case units don't go over with the svg export,laser_arm_mount:Laser arm mount - raised area by arm bearings as a layer,laser_bearing_washer:  washer - if laser cutting it,laser_cam:Laser cam top/bottom - need 2,laser_cam_center:Laser cam center - Stronger - but you need to glue it to top/bottom,laser_bearing_bushing:Laser bearing bushing to make up the difference between bolt_r and bearing_ir - need 2,laser_bldc_motor_standoff:Laser bldc motor has an input shaft that sticks out too far,laser_base_mount_left:Laser base - top plate,laser_base_mount_right:Laser base - bottom plate,laser_paddle:Laser paddle for arm ends - need 2,laser_arm:Laser arms - need 2]


/* [Hidden] */


// Laser parts
param_partl="";



// Don't touch $fn, the param_complexity variable is over-ridden in the makefile
$fn=param_complexity;


// Generates the path for the cam.  The cam surface is generated by subtraction of the cam bearing from the surface
// while rotating both the cam and the arms.  This is the angle to rotate between steps when generating this.
// Smaller values result in smoother, but more complicated surfaces.  
// A good value for working is 15. A good value for rendering is 2-5.
path_step=param_path_step; // [115]


// Assembly views, a little broken.
//rotate([90,0,0]) cosv_assembly_view(cam_angle=$t*180,explode=30);
//cam_assembly_view(explode=10);
//flow_sensor_assembly_view(rot=360*$t,explode=0.1);

// The parts.
// Uncomment these to generate them, render, export.
// for the laser files, export as svg.





PART=param_part;

if (PART == "cam") {
	cam(); // cam top/bottom.  Need 2.
} else if (PART == "paddle") {
	paddle(); // paddle for the arms.  Need 2
} else if (PART == "base_mount_right") {
	base_mount_right(); // base plate/motor mount.  Adjust the bolt pattern you need below first.  Need 1.
} else if (PART == "base_mount_left") {
	base_mount_left(); // top plate/electronics mount.  Need 1.
} else if (PART == "bldc_motor_standoff") {
	bldc_motor_standoff(); // bldc motor has a long pilot on it, which requires a standoff. Need 1.
} else if (PART == "arm") {
	arm();
} else if (PART == "supply_cover") {
	supply_cover();
} else if (PART == "flow_sensor_pitot_for_pcb") {
	flow_sensor_pitot_for_pcb();
} else if (PART == "flow_sensor_venturi_for_pcb") {
	flow_sensor_venturi_for_pcb();
} else if (PART == "flow_sensor_cover_oled") {
	flow_sensor_cover(oled=0);
} else if (PART == "flow_sensor_cover") {
	flow_sensor_cover();
} else if (PART == "bearing_bushing") {
	bearing_bushing(); // parts used within the other FFF parts
} else if (PART == "bearing_washer") {
	bearing_washer(); // parts used within the other FFF parts

// Laser parts.  Arms at least should have arm_w (below) turned up as acrylic isn't as strong as FFF.

} else if (PART == "laser_callibration_square_10x10mm") {
	laser_callibration_square(w=10); // A square, 10x10mm in case units don't go over with the svg export.
} else if (PART == "laser_arm_mount") {
	laser_arm_mount(); // raised area by arm bearings as a layer
} else if (PART == "laser_bearing_washer") {
	laser_bearing_washer(); // washer, if laser cutting it
} else if (PART == "laser_cam") {
	laser_cam(); // cam top/bottom
} else if (PART == "laser_cam_center") {
	laser_cam_center(); //cam center.  Stronger, but you need to glue it to top/bottom
} else if (PART == "laser_bearing_bushing") {
	laser_bearing_bushing(); // bushing to make up the difference between bolt_r and bearing_ir
} else if (PART == "laser_bldc_motor_standoff") {
	laser_bldc_motor_standoff(); // bldc motor has an input shaft that sticks out too far
} else if (PART == "laser_base_mount_left") {
	laser_base_mount_left(); // base, top plate
} else if (PART == "laser_base_mount_botom") {
	laser_base_mount_right(); // base, top plate
} else if (PART == "laser_base_end_right") {
	laser_base_end_right(); // base, top plate
} else if (PART == "laser_base_end_left") {
	laser_base_end_left(); // base, top plate
} else if (PART == "laser_base_mount_right") {
} else if (PART == "laser_paddle") {
	laser_paddle(); // paddle for arm ends
} else if (PART == "laser_arm") {
	laser_arm(); // The arms (when symetrical).
} else if (PART == "laser_arm_end_support") {
	laser_arm_end_support(); // The arm end.
}
//laser_base_mount_left(); // base, top plate
//laser_base_mount_right(); // base, top plate
//laser_arm(path_step=1,$fn=90); // base, top plate
//laser_arm_end_support(path_step=1,$fn=90); // extend the normal arm end +z for a stacked solution to flex
//laser_arm_mount(); // base, top plate
//laser_base_end_right(slots=0); // base, top plate
//laser_base_end_left(slots=0); // base, top plate
//laser_base_front_analog(); // base front
//laser_base_front_pi(layer=0); // base front

//laser_base_front(); // base front
laser_base_front_pi(layer=0); // base front
//laser_base_front_pi(layer=1); // base front
//laser_base_front_pi(layer=2); // base front
//laser_base_back_wiper(); // base back
//laser_base_back(); // base back
//laser_cam_end_plate_t(); // base back
//laser_cam_end_plate_b(); // base back
//laser_cam_center_b(); // base back
//laser_cam_center_t(); // base back
//laser_bearing_bushing(r=6/2); // parts used within the other FFF parts
//laser_base_top();
//laser_base_right();
//laser_cam_encoder();

//cam(); // cam top/bottom.  Need 2.
//paddle(); // paddle for the arms.  Need 2
//base_mount_right(); // base plate/motor mount.  Adjust the bolt pattern you need below first.  Need 1.
//base_mount_left(); // base plate opposite motor mount. Need 1.
//base_end_left(); // base end plate/bag mounts.  Need 1, top bag end diameter.
//base_plate(); // top plate/electronics mount.  Need 1.
//base_front_analog(); // top plate/electronics mount.  Need 1.
//base_front_pi(layer=1); // top plate/electronics mount.  Need 1.
//base_back(); // top plate/electronics mount.  Need 1.
//base_top();
//arm();
//cam_encoder(h=0.5);
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

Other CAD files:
hardware/rendered/Laser/kerf_0.15_mat_3.0/laser_paddle_layer_1.dxf
hardware/rendered/FFF/flow_sensor_for_pcb.stl
hardware/rendered/Laser/kerf_0.04_mat_3.0/laser_base_mount_left.dxf
hardware/rendered/Laser/kerf_0.15_mat_3.0/laser_base_end_left_inner.dxf
hardware/rendered/Laser/kerf_0.04_mat_3.0/laser_arm.dxf
hardware/rendered/Laser/kerf_0.04_mat_3.0/laser_arm_end_support.dxf
hardware/rendered/Laser/kerf_0.04_mat_3.0/laser_arm_mount_left.dxf
hardware/rendered/Laser/kerf_0.04_mat_3.0/laser_arm_mount_right.dxf
hardware/rendered/Laser/kerf_0.04_mat_3.0/laser_base_back.dxf
hardware/rendered/Laser/kerf_0.04_mat_3.0/laser_base_back_wiper.dxf
hardware/rendered/Laser/kerf_0.04_mat_3.0/laser_base_battery_mount_bottom.dxf
hardware/rendered/Laser/kerf_0.04_mat_3.0/laser_base_battery_mount_top.dxf
hardware/rendered/Laser/kerf_0.04_mat_3.0/laser_base_bottom.dxf
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

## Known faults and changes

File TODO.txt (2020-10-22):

Cam Arms can lock up and break the machine, eliminate manual grinding step by changing profile of arm. - Done
Enlarge heat sink model for IBT_2 (Manufacturing tolerances, it's too tight on one of Steve's IBT_2's).
Move IBT_2 slightly away from the wiper motor (PCB is shorting out to the motor housing)
Enlarge wiper motor housing by a millimeter to take into consideration manufacturing differences
Enlarge battery model slightly.  Steven has 5 batteries and none of them are the exact same size.  Tops are glued on slightly offset, etc.
Battery removal panel.  Let's be able to take the battery out without taking the whole thing apart.
Battery swelling: If battery is overcharged and fails, it will swell.  This should bulge/break a battery door, not destroy the whole side of the unit.
Battery spacers (Need 10, 5 top, 5 bottom) to prevent the battery from hitting the twin nuts.   Taper the edges to the 5/16" bolts for clearance near the display. Note: this gives us room in that area to put power electronics!  Easy to get to with the battery door removed!
Battery cage from stacking battery mounts and new mount spacers (just washers made from the laser cut material)
Display panel screws break the display when the unit is dropped.  They are too close to the edge of the glass.
Transparent display cover?   Removable via Magnetically attach points?  Protect the flimsy display from being broken when hauling the thing around.
Snap in power switch
Tombstone RJ45 hookup for VISP needs to be located somewhere better.  Hard to install on battery side unless it is in a housing on the top of the upper plate with RJ45 facing out of the side (Not a bad idea). Battery mounts may make this awkward to route the cable to the Carrier. Maybe include USB port to go to the rPi so we can attach a keyboard/mouse, or USB key for firmware updating.

Internal arm guides (3 on each side)
Handle is too close to the bag.
Bag cover.  Any pressing of the bag WILL trigger an unwanted inhalation cycle.   We have to protect it from being bumped around in the chopper, or on the pole going down the hallway/into elevators, etc
Pole clamp.   Need to figure out how to do this without redesigning the whole unit.  (Also, bedside hooks?)

Aluminum cam-to-motor part.  Perhaps a 6MM x 25MM machined part with integrated threads for the skate bearings? At least a pair of pockets like the existing system.  If AL, maybe threaded inserts in a stronger material?

Optical encoder mount?   Something (anything) to make the encoder easier to add after the cam part is put together.  Maybe a 3D printed mount?  It needs to mount to the side of the cam housing, and then permit the encoder to mount to it.  We only have 8MM to work with.  Maybe the encoder PCB should be shaped like a T with 2 mount holes on the left/right of the top of the T?

Ford wiper motor cable harness.  Let's make a 3D printed spade terminal wiring harness that just works, without the end assembler getting lines crossed, or hooked up wrong inadvertantly.  Eliminate problems now, with a little bit of investment.
Carrier (3d printed or PCB) for twin buck/boost converters for battery charging/rPi-power mounting under the motor or behind the battery on the cam plate.   Something to make assembly dirt simple.
Somehow eliminate tuning of buck/boost boards. We cannot trust the end user/packager to do this properly.  Should 5V converter be placed on the rPi carrier board?
Select and standardize on power jack and power supply.  Needs to be completely removable from the back of the unit, but only when wanted.  Could have a simple retaining clip/zip tie/velcro holder.
Design the alarm circuits.  Needs 2 different alarm sounds for the Critical (Patient not exhaling) vs Warning (battery low)

VISP board: add integrated RJ45, so we don't have to solder wires, we can use any standard ethernet cable.
VISP board: Getting to the screw under the LCD requires that the LCD be removable, or attached via a small ribbon cable.  The ribbon cable is a PITA to assemble.

Investigate "tube compliance check", might require mods to the machine.

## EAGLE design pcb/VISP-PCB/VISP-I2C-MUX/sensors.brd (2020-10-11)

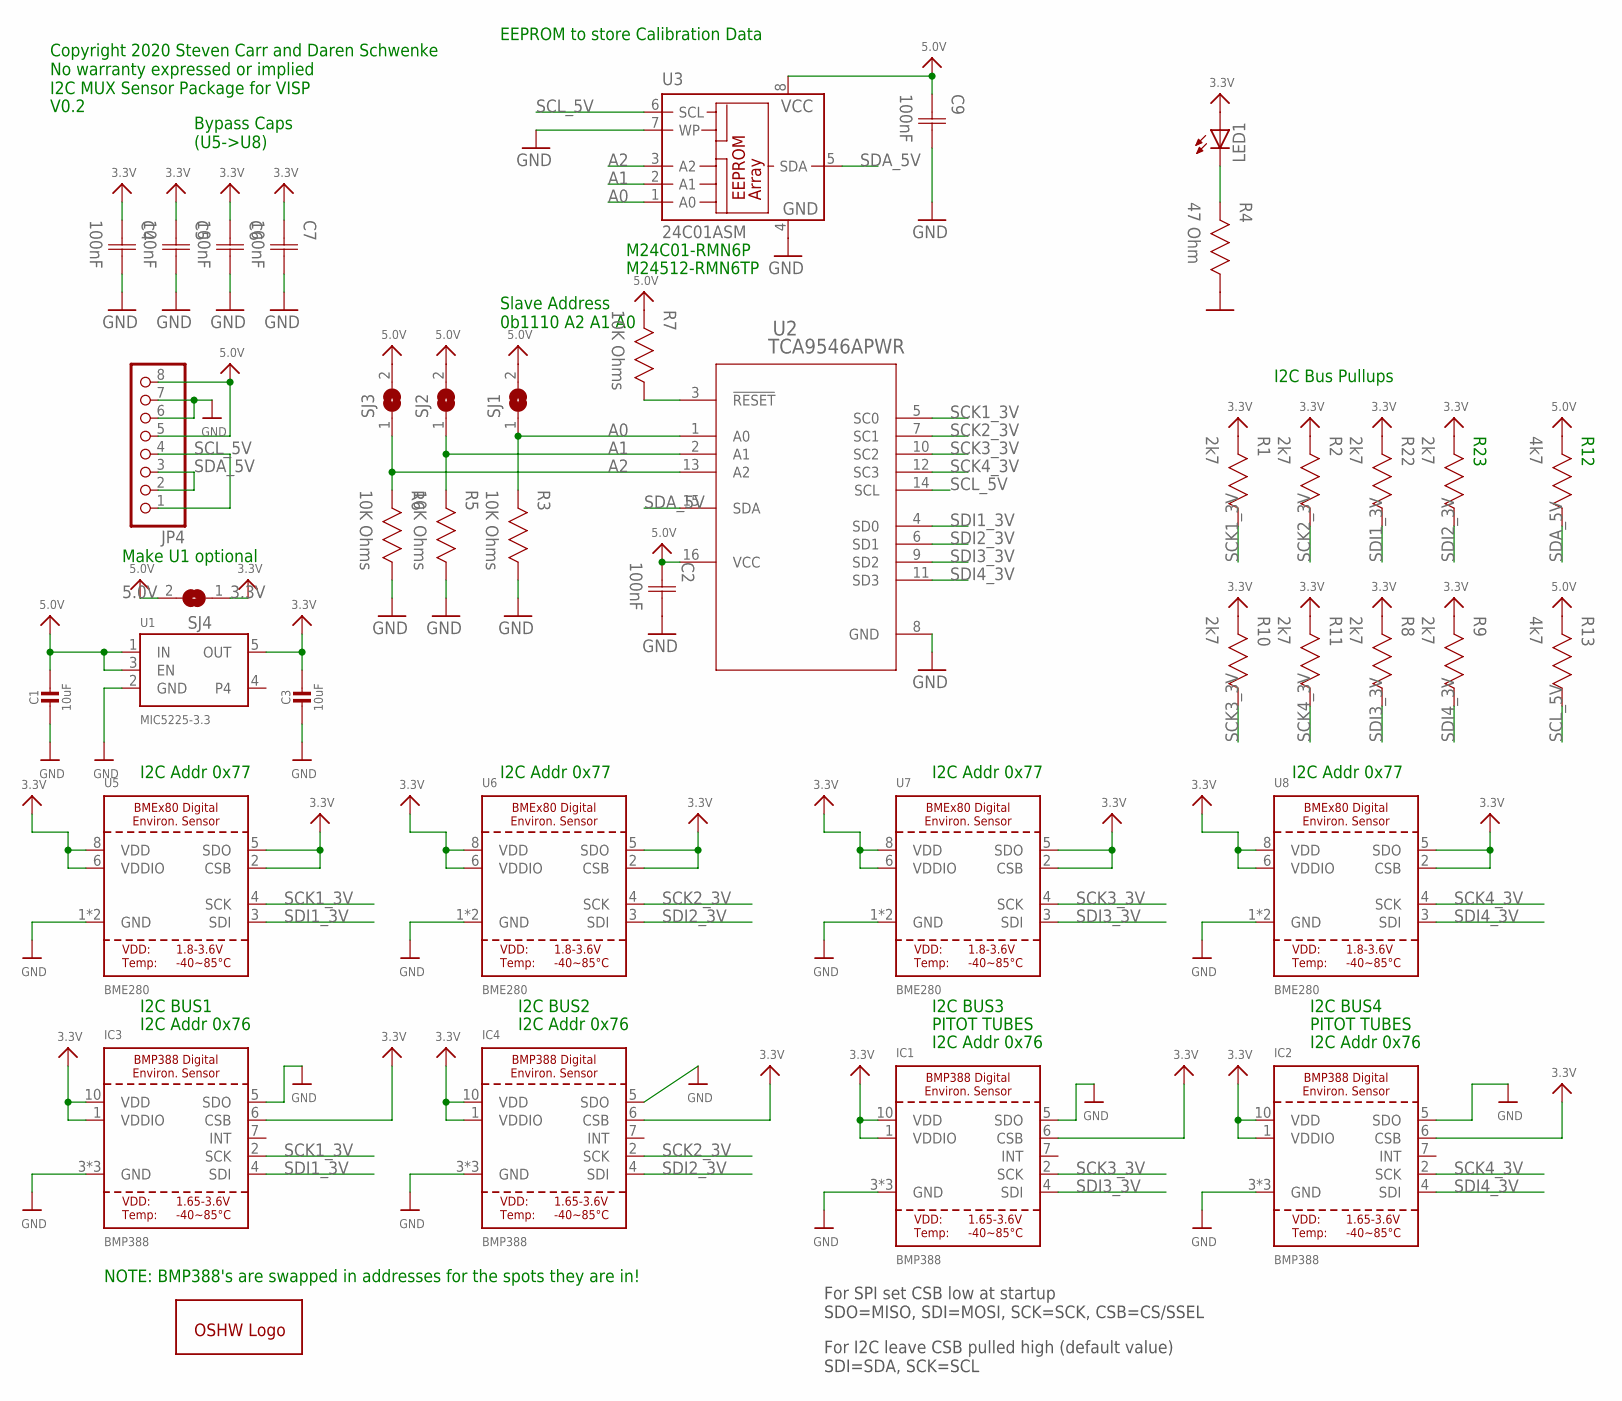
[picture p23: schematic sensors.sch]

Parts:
C1, C3: 10uF; _0805; MPN C1608X5R1A106M080AC
C2, C9: 100nF; CAP0402; MPN CL10B104KB8NNNC
C4, C5, C6, C7: 100nF; CAP0402; MPN CL10F104ZO8NNNC
GOLD_ORB_SM1: OSHWLOGOLOGO8MM; OSHW_8MM
IC1, IC2, IC3, IC4: BMP388; MPN BMP388
JP4: PINHD-1X08_2.54; 1X08
LED1: LEDCHIP-LED0603; CHIP-LED0603; MPN SML-D12P8WT86
R1, R2, R8, R9, R10, R11, R22, R23: 2k7; RES0402; MPN CRCW060310K0FKEAC
R3, R5, R6, R7: 10K Ohms; RES0402; MPN CRCW060310K0FKEAC
R4: 47 Ohm; RES0402; MPN RC0603FR-0747RL
R12, R13: 4k7; RES0402; MPN CRCW060310K0FKEAC
SJ1, SJ2, SJ3, SJ4: SJ
U1: MIC5225-3.3; SOT23-5; MPN MIC5225-3.3YM5-TR
U2: TCA9546APWR; PW16
U3: 24C01ASM; SO-08M; MPN M24C01-RMN6P
U5, U6, U7, U8: BME280

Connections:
3.3V: C3.1, C4.1 (C1), C5.1 (C1), C6.1 (C1), C7.1 (C1), IC1.1 (VDDIO), IC1.6 (CSB), IC1.10 (VDD), IC2.1 (VDDIO), IC2.6 (CSB), IC2.10 (VDD), IC3.1 (VDDIO), IC3.6 (CSB), IC3.10 (VDD), IC4.1 (VDDIO), IC4.6 (CSB), IC4.10 (VDD), LED1.A, R1.2, R2.2, R8.2, R9.2, R10.2, R11.2, R22.2, R23.2, SJ4.1, U1.5 (OUT), U5.2 (CSB), U5.5 (SDO), U5.6 (VDDIO), U5.8 (VDD), U6.2 (CSB), U6.5 (SDO), U6.6 (VDDIO), U6.8 (VDD), U7.2 (CSB), U7.5 (SDO), U7.6 (VDDIO), U7.8 (VDD), U8.2 (CSB), U8.5 (SDO), U8.6 (VDDIO), U8.8 (VDD)
5.0V: C1.1, C2.1 (C1), C9.1 (C1), JP4.5, JP4.8, R7.2, R12.2, R13.2, SJ1.2, SJ2.2, SJ3.2, SJ4.2, U1.1 (IN), U1.3 (EN), U2.16 (VCC), U3.8 (VCC)
A0: R3.2, SJ1.1, U2.1 (A0), U3.1 (A0)
A1: R5.2, SJ2.1, U2.2 (A1), U3.2 (A1)
A2: R6.2, SJ3.1, U2.13 (A2), U3.3 (A2)
GND: C1.2, C2.2 (C2), C3.2, C4.2 (C2), C5.2 (C2), C6.2 (C2), C7.2 (C2), C9.2 (C2), IC1.3 (GND), IC1.5 (SDO), IC1.8 (GND), IC1.9 (GND), IC2.3 (GND), IC2.5 (SDO), IC2.8 (GND), IC2.9 (GND), IC3.3 (GND), IC3.5 (SDO), IC3.8 (GND), IC3.9 (GND), IC4.3 (GND), IC4.5 (SDO), IC4.8 (GND), IC4.9 (GND), JP4.6, JP4.7, R3.1, R4.1, R5.1, R6.1, U1.2 (GND), U2.8 (GND), U3.4 (GND), U3.7 (WP), U5.1 (GND), U5.7 (GND), U6.1 (GND), U6.7 (GND), U7.1 (GND), U7.7 (GND), U8.1 (GND), U8.7 (GND)
LED: LED1.C, R4.2
RESET: R7.1, U2.3 (!RESET)
SCK1_3V: IC3.2 (SCK), R1.1, U2.5 (SC0), U5.4 (SCK)
SCK2_3V: IC4.2 (SCK), R2.1, U2.7 (SC1), U6.4 (SCK)
SCK3_3V: IC1.2 (SCK), R10.1, U2.10 (SC2), U7.4 (SCK)
SCK4_3V: IC2.2 (SCK), R11.1, U2.12 (SC3), U8.4 (SCK)
SCL_5V: JP4.1, JP4.4, R13.1, U2.14 (SCL), U3.6 (SCL)
SDA_5V: JP4.2, JP4.3, R12.1, U2.15 (SDA), U3.5 (SDA)
SDI1_3V: IC3.4 (SDI), R22.1, U2.4 (SD0), U5.3 (SDI)
SDI2_3V: IC4.4 (SDI), R23.1, U2.6 (SD1), U6.3 (SDI)
SDI3_3V: IC1.4 (SDI), R8.1, U2.9 (SD2), U7.3 (SDI)
SDI4_3V: IC2.4 (SDI), R9.1, U2.11 (SD3), U8.3 (SDI)

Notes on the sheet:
Bypass Caps (U5->U8)
Copyright 2020 Steven Carr and Daren Schwenke No warranty expressed or implied I2C MUX Sensor Package for VISP
EEPROM to store Calibration Data
V0.2
Make U1 optional
For SPI set CSB low at startup SDO=MISO, SDI=MOSI, SCK=SCK, CSB=CS/SSEL
For I2C leave CSB pulled high (default value) SDI=SDA, SCK=SCL
M24C01-RMN6P
M24512-RMN6TP
I2C Bus Pullups
Slave Address 0b1110 A2 A1 A0
I2C Addr 0x76
PITOT TUBES
I2C Addr 0x77
I2C BUS1
I2C BUS2
I2C BUS3
I2C BUS4
NOTE: BMP388's are swapped in addresses for the spots they are in!

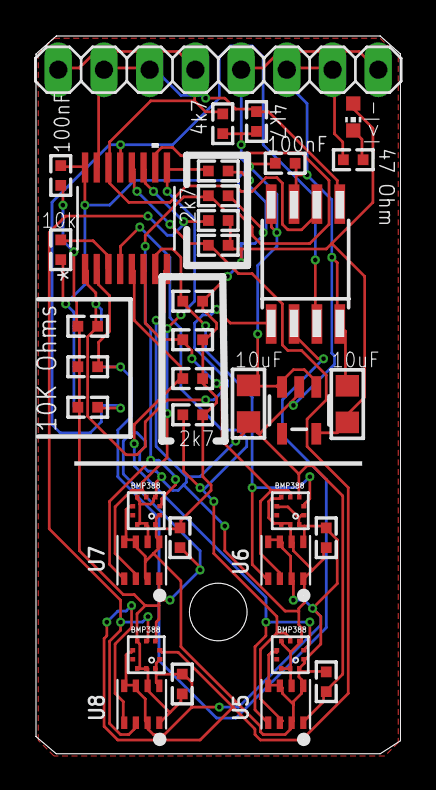
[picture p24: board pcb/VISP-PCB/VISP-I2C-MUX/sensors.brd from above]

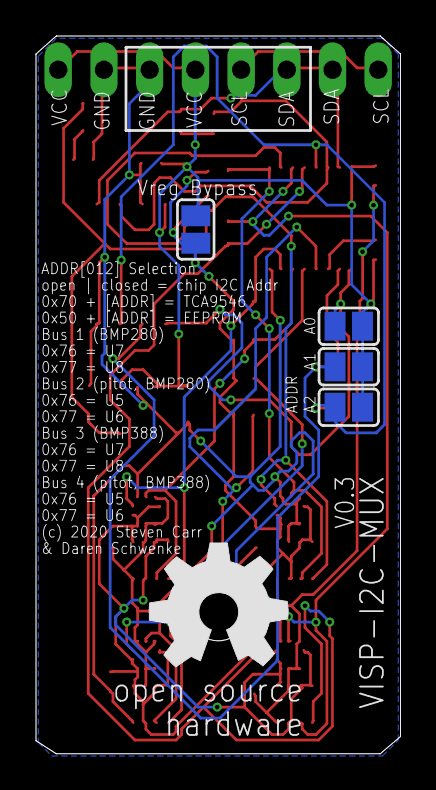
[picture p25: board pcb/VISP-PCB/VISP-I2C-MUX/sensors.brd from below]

Board: 2 copper layers, 20.2 x 39.9 mm, 41 parts (5 on the bottom side), 18 nets.

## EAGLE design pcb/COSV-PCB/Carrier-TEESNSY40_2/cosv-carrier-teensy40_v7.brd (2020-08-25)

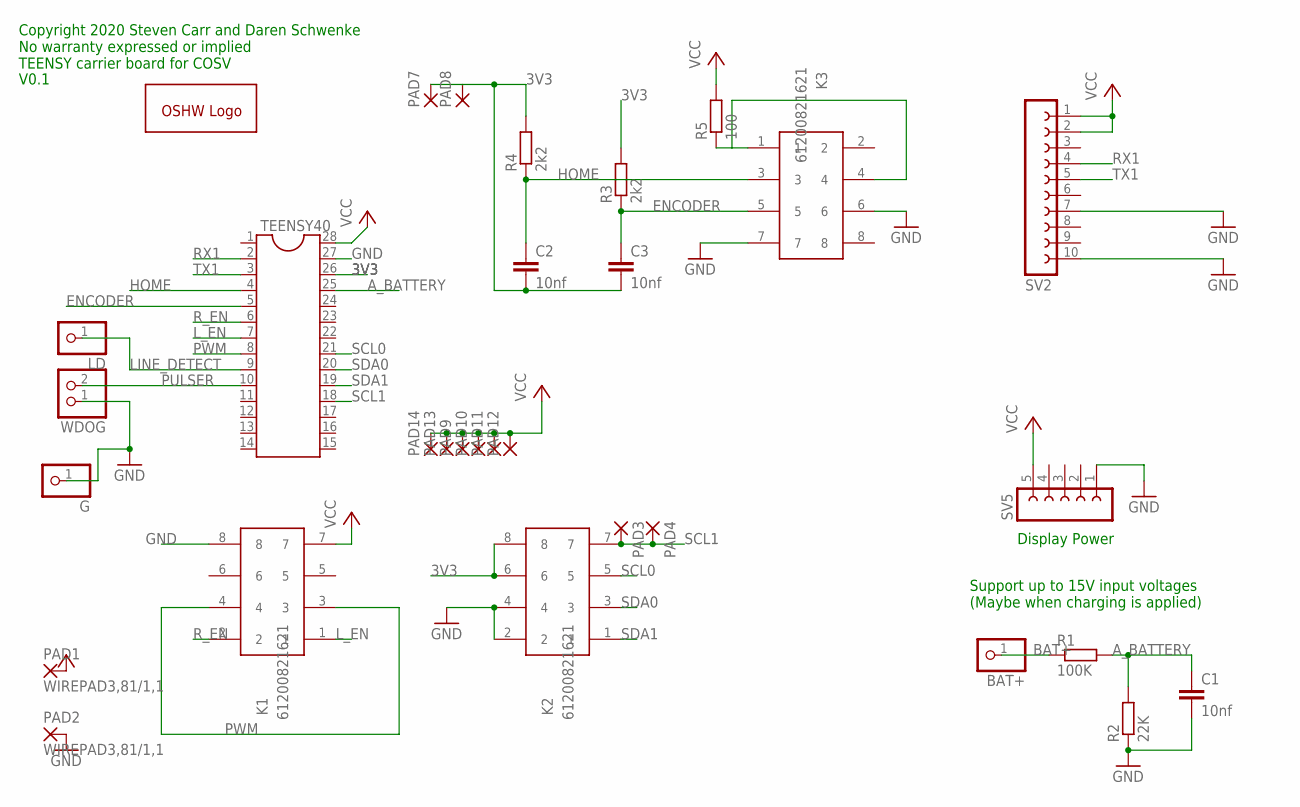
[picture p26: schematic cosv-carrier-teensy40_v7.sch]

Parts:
BAT+: PINHD-1X01_2.54-S; 1X01-S
C1, C2, C3: 10nf; C1206
G: PINHD-1X01_2.54-S; 1X01-S
GOLD_ORB_SM1: OSHWLOGOLOGO8MM; OSHW_8MM
K1, K2, K3: 61200821621
LD: PINHD-1X01_2.54-S; 1X01-S
PAD1, PAD2: WIREPAD3,81/1,1; 3,81/1,1
PAD3, PAD4, PAD7, PAD8, PAD9, PAD10, PAD11, PAD12, PAD13, PAD14: 1,6/0,9
R1: 100K; R1206
R2: 22K; R1206
R3, R4: 2k2; R1206
R5: 100; R1206
SV2: FE10-1; FE10
SV5: FE05W
TEENSY40: DIL28; DIL28-6
WDOG: PINHD-1X2; 1X02

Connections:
3V3: C2.2, C3.2, K2.6, K2.8, PAD7.1, PAD8.1, R3.2, R4.2, TEENSY40.26
A_BATTERY: C1.1, R1.2, R2.2, TEENSY40.25
BAT+: BAT+.1, R1.1
ENCODER: C3.1, K3.5, R3.1, TEENSY40.5
GND: C1.2, G.1, K1.8, K2.2, K2.4, K3.6, K3.7, PAD2.1, R2.1, SV2.7, SV2.10, SV5.1, TEENSY40.27, WDOG.1
HOME: C2.1, K3.3, R4.1, TEENSY40.4
LED: K3.1, K3.4, R5.1
LINE_DETECT: LD.1, TEENSY40.9
L_EN: K1.1, TEENSY40.7
PULSER: TEENSY40.10, WDOG.2
PWM: K1.3, K1.4, TEENSY40.8
RX1: SV2.4, TEENSY40.2
R_EN: K1.2, TEENSY40.6
SCL0: K2.5, TEENSY40.21
SCL1: K2.7, PAD3.1, PAD4.1, TEENSY40.18
SDA0: K2.3, TEENSY40.20
SDA1: K2.1, TEENSY40.19
TX1: SV2.5, TEENSY40.3
VCC: K1.7, PAD1.1, PAD9.1, PAD10.1, PAD11.1, PAD12.1, PAD13.1, PAD14.1, R5.2, SV2.1, SV2.2, SV5.5, TEENSY40.28

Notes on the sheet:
Display Power
Support up to 15V input voltages (Maybe when charging is applied)
Copyright 2020 Steven Carr and Daren Schwenke No warranty expressed or implied TEENSY carrier board for COSV
V0.1

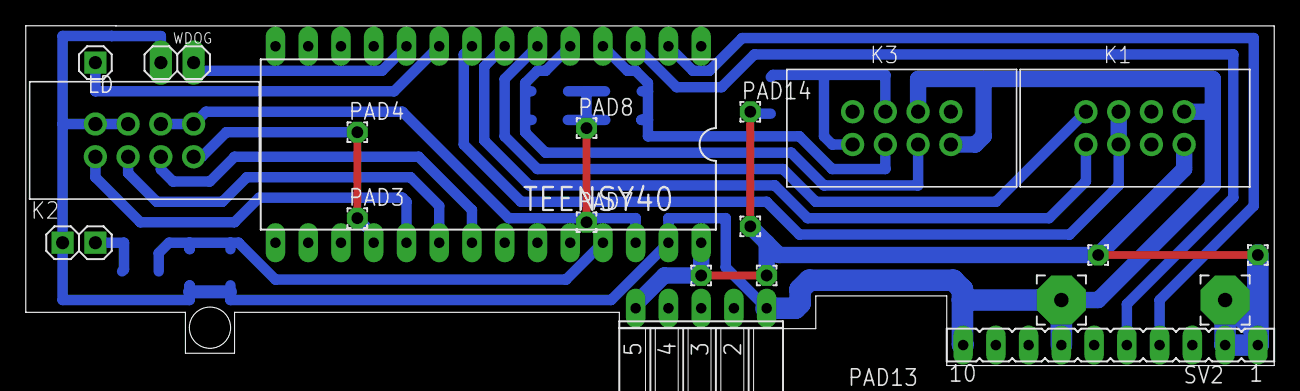
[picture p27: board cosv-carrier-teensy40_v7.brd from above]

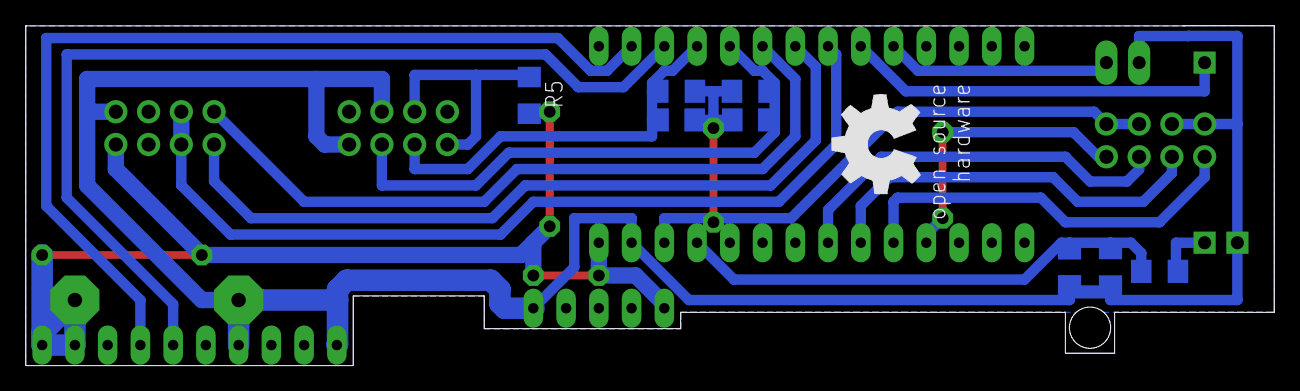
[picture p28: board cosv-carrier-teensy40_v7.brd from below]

Board: 2 copper layers, 96.8 x 26.4 mm, 31 parts (9 on the bottom side), 19 nets.

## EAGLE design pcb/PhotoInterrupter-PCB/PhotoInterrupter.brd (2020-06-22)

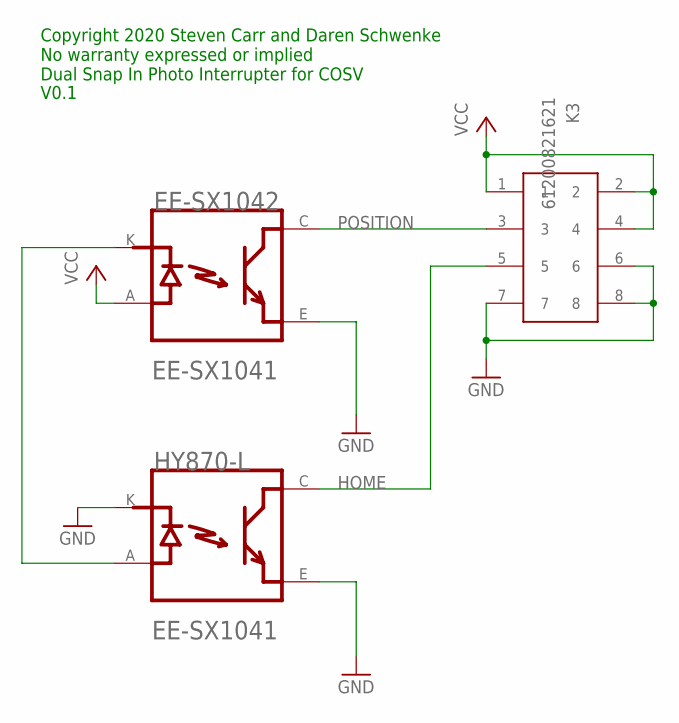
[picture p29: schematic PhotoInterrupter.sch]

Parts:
EE-SX1042: OMRON_ELECTRONICS_INC-EMC_DIV_EE-SX1041OMRON_ELEC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; OMRON_ELECTRONICS_INC-EMC_DIV_EE-SX1041_0
HY870-L: OMRON_ELECTRONICS_INC-EMC_DIV_EE-SX1041OMRON_ELEC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; OMRON_ELECTRONICS_INC-EMC_DIV_EE-SX1041_0
K3: 61200821621

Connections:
GND: EE-SX1042.E, HY870-L.E, HY870-L.K, K3.6, K3.7, K3.8
HOME: HY870-L.C, K3.5
unnamed: EE-SX1042.K, HY870-L.A
POSITION: EE-SX1042.C, K3.3
VCC: EE-SX1042.A, K3.1, K3.2, K3.4

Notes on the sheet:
Copyright 2020 Steven Carr and Daren Schwenke No warranty expressed or implied Dual Snap In Photo Interrupter for COSV
V0.1

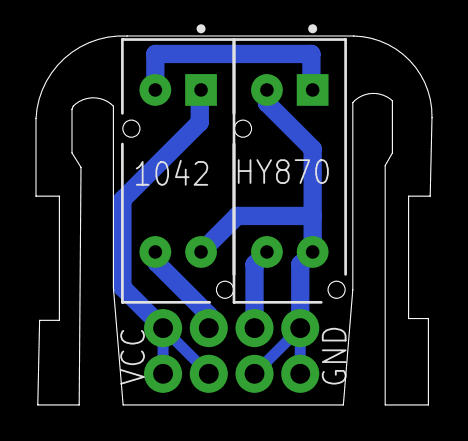
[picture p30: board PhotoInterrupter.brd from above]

Board: 2 copper layers, 22.0 x 20.5 mm, 3 parts (1 on the bottom side), 5 nets.

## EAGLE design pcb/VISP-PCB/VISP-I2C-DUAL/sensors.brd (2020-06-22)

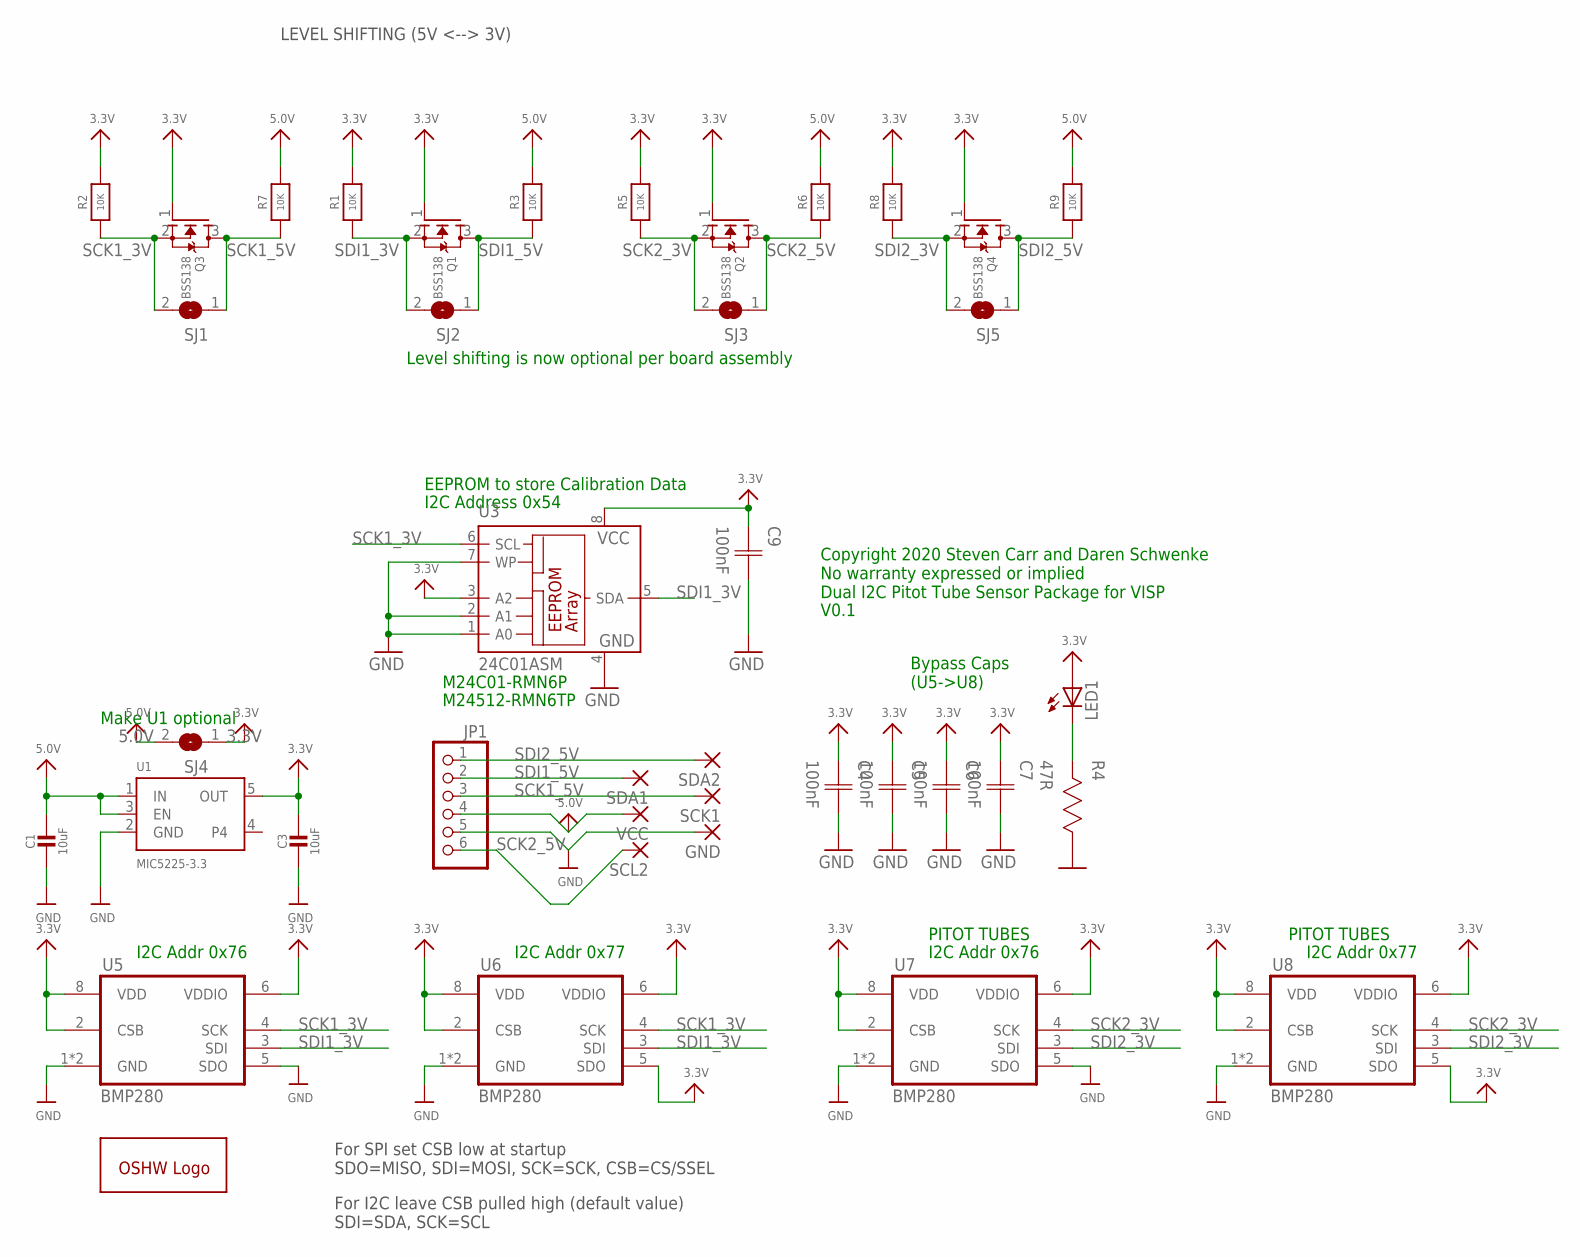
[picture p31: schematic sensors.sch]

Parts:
C1, C3: 10uF; _0805; MPN C1608X5R1A106M080AC
C4, C5, C6, C7: 100nF; CAP0402; MPN CL10F104ZO8NNNC
C9: 100nF; CAP0402; MPN CL10B104KB8NNNC
GND: SMD2; SMD1,27-2,54
GOLD_ORB_SM1: OSHWLOGOLOGO8MM; OSHW_8MM
JP1: PINHD-1X6; 1X06
LED1: LEDCHIP-LED0603; CHIP-LED0603; MPN SML-D12P8WT86
Q1, Q2, Q3, Q4: BSS138; SOT23-WIDE
R1, R2, R3, R5, R6, R7, R8, R9: 10K; _0402
R4: 47R; RES0402; MPN RC0603FR-0747RL
SCK1: SMD2; SMD1,27-2,54
SCL2: SMD2; SMD1,27-2,54
SDA1, SDA2: SMD2; SMD1,27-2,54
SJ1, SJ2, SJ3, SJ4, SJ5: SJ
U1: MIC5225-3.3; SOT23-5; MPN MIC5225-3.3YM5-TR
U3: 24C01ASM; SO-08M; MPN M24C01-RMN6P
U5, U6, U7, U8: BMP280; MPN BMP280
VCC: SMD2; SMD1,27-2,54

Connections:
3.3V: C3.1, C4.1 (C1), C5.1 (C1), C6.1 (C1), C7.1 (C1), C9.1 (C1), LED1.A, Q1.1 (G), Q2.1 (G), Q3.1 (G), Q4.1 (G), R1.2, R2.2, R5.2, R8.2, SJ4.1, U1.5 (OUT), U3.3 (A2), U3.8 (VCC), U5.2 (CSB), U5.6 (VDDIO), U5.8 (VDD), U6.2 (CSB), U6.5 (SDO), U6.6 (VDDIO), U6.8 (VDD), U7.2 (CSB), U7.6 (VDDIO), U7.8 (VDD), U8.2 (CSB), U8.5 (SDO), U8.6 (VDDIO), U8.8 (VDD)
5.0V: C1.1, JP1.4, R3.2, R6.2, R7.2, R9.2, SJ4.2, U1.1 (IN), U1.3 (EN), VCC.1
GND: C1.2, C3.2, C4.2 (C2), C5.2 (C2), C6.2 (C2), C7.2 (C2), C9.2 (C2), GND.1, JP1.5, R4.1, U1.2 (GND), U3.1 (A0), U3.2 (A1), U3.4 (GND), U3.7 (WP), U5.1 (GND), U5.5 (SDO), U5.7 (GND), U6.1 (GND), U6.7 (GND), U7.1 (GND), U7.5 (SDO), U7.7 (GND), U8.1 (GND), U8.7 (GND)
LED: LED1.C, R4.2
SCK1_3V: Q3.2 (S), R2.1, SJ1.2, U3.6 (SCL), U5.4 (SCK), U6.4 (SCK)
SCK1_5V: JP1.3, Q3.3 (D), R7.1, SCK1.1, SJ1.1
SCK2_3V: Q2.2 (S), R5.1, SJ3.2, U7.4 (SCK), U8.4 (SCK)
SCK2_5V: JP1.6, Q2.3 (D), R6.1, SCL2.1, SJ3.1
SDI1_3V: Q1.2 (S), R1.1, SJ2.2, U3.5 (SDA), U5.3 (SDI), U6.3 (SDI)
SDI1_5V: JP1.2, Q1.3 (D), R3.1, SDA1.1, SJ2.1
SDI2_3V: Q4.2 (S), R8.1, SJ5.2, U7.3 (SDI), U8.3 (SDI)
SDI2_5V: JP1.1, Q4.3 (D), R9.1, SDA2.1, SJ5.1

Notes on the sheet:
Bypass Caps (U5->U8)
Copyright 2020 Steven Carr and Daren Schwenke No warranty expressed or implied Dual I2C Pitot Tube Sensor Package for VISP
I2C Addr 0x76
I2C Addr 0x77
V0.1
Make U1 optional
PITOT TUBES
For SPI set CSB low at startup SDO=MISO, SDI=MOSI, SCK=SCK, CSB=CS/SSEL
For I2C leave CSB pulled high (default value) SDI=SDA, SCK=SCL
EEPROM to store Calibration Data
M24C01-RMN6P
M24512-RMN6TP
I2C Address 0x54
LEVEL SHIFTING (5V <--> 3V)
Level shifting is now optional per board assembly

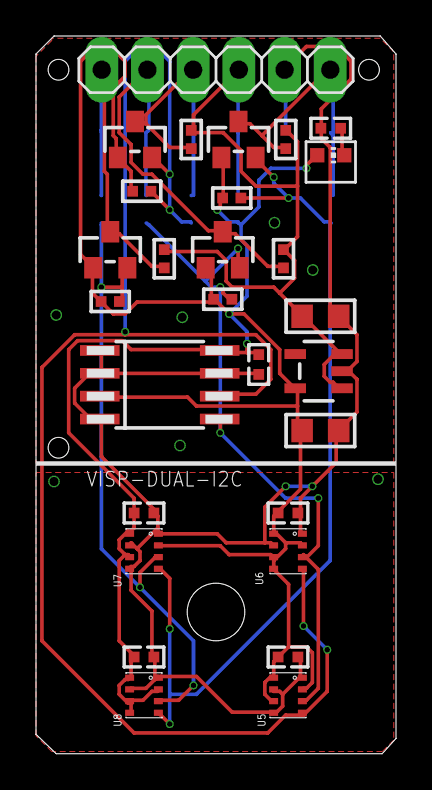
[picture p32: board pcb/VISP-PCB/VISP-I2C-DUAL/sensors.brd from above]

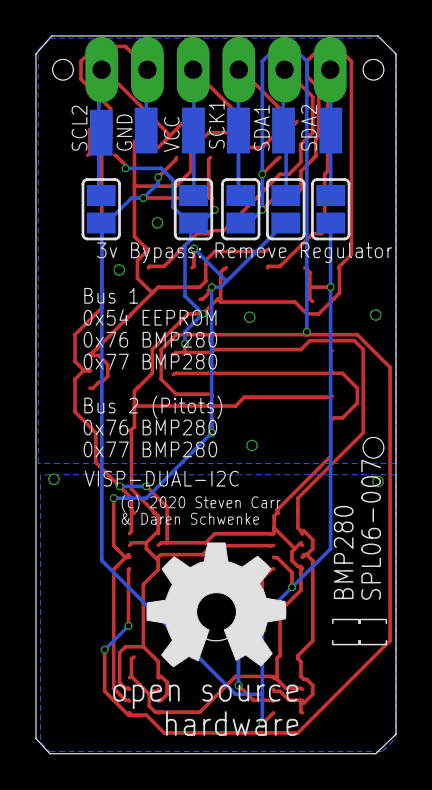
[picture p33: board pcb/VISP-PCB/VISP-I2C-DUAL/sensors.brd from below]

Board: 2 copper layers, 20.0 x 39.9 mm, 40 parts (12 on the bottom side), 12 nets.

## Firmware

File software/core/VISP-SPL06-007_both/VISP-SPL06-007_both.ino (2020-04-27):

/*
   This file is part of VISP.

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
   You should have received a copy of the GNU General Public License
   along with Cleanflight.  If not, see <http://www.gnu.org/licenses/>.
*/
#define TEENSY 1
#include <math.h>
#include <stdbool.h>
#include <stdint.h>
#include <Wire.h>
#include <SPI.h>




// Chip type detection
#define DETECTION_MAX_RETRY_COUNT   5


typedef enum {
  BUSTYPE_ANY  = 0,
  BUSTYPE_NONE = 0,
  BUSTYPE_I2C  = 1,
  BUSTYPE_SPI  = 2
} busType_e;

typedef enum {
  HWTYPE_NONE = 0,
  HWTYPE_SENSOR  = 1,
  HWTYPE_MUX  = 2
} hwType_e;

typedef struct busDevice_s {
  busType_e busType;
  hwType_e hwType;
  uint8_t currentChannel; // If this device is a HWTYPE_MUX
  union {
    struct {
      SPIClass *spiBus;            // SPI bus
      uint8_t csnPin;         // IO for CS# pin
    } spi;
    struct {
      TwoWire *i2cBus;        // I2C bus ID
      uint8_t address;        // I2C bus device address
      uint8_t channel;        // MUXed I2C Channel
      struct busDevice_s *channelDev; // MUXed I2C Channel Address
    } i2c;
  } busdev;
} busDevice_t;


typedef struct bmp280_calib_param_s {
  uint16_t dig_T1; /* calibration T1 data */
  int16_t dig_T2; /* calibration T2 data */
  int16_t dig_T3; /* calibration T3 data */
  uint16_t dig_P1; /* calibration P1 data */
  int16_t dig_P2; /* calibration P2 data */
  int16_t dig_P3; /* calibration P3 data */
  int16_t dig_P4; /* calibration P4 data */
  int16_t dig_P5; /* calibration P5 data */
  int16_t dig_P6; /* calibration P6 data */
  int16_t dig_P7; /* calibration P7 data */
  int16_t dig_P8; /* calibration P8 data */
  int16_t dig_P9; /* calibration P9 data */
  int32_t t_fine; /* calibration t_fine data */
} bmp280_calib_param_t;

// SPL06, address 0x76

typedef struct {
  int16_t c0;
  int16_t c1;
  int32_t c00;
  int32_t c10;
  int16_t c01;
  int16_t c11;
  int16_t c20;
  int16_t c21;
  int16_t c30;
} spl06_coeffs_t;


struct baroDev_s;
typedef bool (*baroOpFuncPtr)(struct baroDev_s * baro);
typedef bool (*baroCalculateFuncPtr)(struct baroDev_s * baro, float *pressure, float *temperature);


typedef struct baroDev_s {
  busDevice_t * busDev;
  baroCalculateFuncPtr calculate;

  bmp280_calib_param_t bmp280_cal;
  // uncompensated pressure and temperature
  int32_t bmp280_up;
  int32_t bmp280_ut;
  //error free measurements
  int32_t bmp280_up_valid;
  int32_t bmp280_ut_valid;

  spl06_coeffs_t spl06_cal;
  // uncompensated pressure and temperature
  int32_t spl06_pressure_raw;
  int32_t spl06_temperature_raw;
} baroDev_t;



uint8_t muxSelectChannel(busDevice_t *busDev, uint8_t channel)
{
  if (busDev && channel > 0 && channel < 5)
  {
    if (busDev->currentChannel != channel)
    {
      busDev->busdev.i2c.i2cBus->beginTransmission(busDev->busdev.i2c.address);
      busDev->busdev.i2c.i2cBus->write(1 << (channel - 1));
      return busDev->busdev.i2c.i2cBus->endTransmission();
    }
    return 0;
  }
  else {
    return 0xff;
  }
}


void busPrint(busDevice_t *bus, const char *function)
{
  Serial1.print(function);
  if (bus->busType == BUSTYPE_I2C)
  {
    Serial1.print("(I2C:");
    Serial1.print(" address=");
    Serial1.print(bus->busdev.i2c.address);
    // MUX based VISP
    if (bus->busdev.i2c.channel)
    {
      Serial1.print(" channel=");
      Serial1.print(bus->busdev.i2c.channel);
    }
    Serial1.println(")");
    return;
  }
  if (bus->busType == BUSTYPE_SPI)
  {
    Serial1.print("(SPI CSPIN=");
    Serial1.print(bus->busdev.spi.csnPin);
    Serial1.println(")");
    return;
  }
}

busDevice_t *busDeviceInitI2C(TwoWire *wire, uint8_t address, uint8_t channel = 0, busDevice_t *channelDev = NULL)
{
  busDevice_t *dev = (busDevice_t *)malloc(sizeof(busDevice_t));
  memset(dev, 0, sizeof(busDevice_t));
  dev->busType = BUSTYPE_I2C;
  dev->busdev.i2c.i2cBus = wire;
  dev->busdev.i2c.address = address;
  dev->busdev.i2c.channel = channel; // If non-zero, then it is a channel on a TCA9546 at mux
  dev->busdev.i2c.channelDev = channelDev;
  return dev;
}

busDevice_t *busDeviceInitSPI(SPIClass *spiBus, uint8_t csnPin)
{
  busDevice_t *dev = (busDevice_t *)malloc(sizeof(busDevice_t));
  memset(dev, 0, sizeof(busDevice_t));
  dev->busType = BUSTYPE_SPI;
  dev->busdev.spi.spiBus = spiBus;
  dev->busdev.spi.csnPin = csnPin;
  return dev;
}

// TODO: check to see if this is a mux...
void busDeviceFree(busDevice_t *dev)
{
  free(dev);
}



char busReadBuf(busDevice_t *busDev, unsigned char reg, unsigned char *values, uint8_t length)
{
  char x;
  int error;

  if (busDev->busType == BUSTYPE_I2C)
  {
    uint8_t address = busDev->busdev.i2c.address;
    TwoWire *wire = busDev->busdev.i2c.i2cBus;

    muxSelectChannel(busDev->busdev.i2c.channelDev, busDev->busdev.i2c.channel);

    wire->beginTransmission(address);
    wire->write(reg);
    if (0 == (error = wire->endTransmission()))
    {
      wire->requestFrom(address, length);
      while (wire->available() != length) ; // wait until bytes are ready
      for (x = 0; x < length; x++)
      {
        values[x] = wire->read();
      }
      return (1);
    }
    Serial1.print("endTransmission() returned ");
    Serial1.println(error);
    return (0);
  }
  return (0);
}

char busWriteBuf(busDevice_t *busDev, unsigned char reg, unsigned char *values, char length)
{
  if (busDev->busType == BUSTYPE_I2C)
  {
    int address = busDev->busdev.i2c.address;
    TwoWire *wire = busDev->busdev.i2c.i2cBus;

    muxSelectChannel(busDev->busdev.i2c.channelDev, busDev->busdev.i2c.channel);

    wire->beginTransmission(address);
    wire->write(values, length);
    if (0 == wire->endTransmission())
      return (1);
    else
      return (0);
  }
  return 1;
}


char busRead(busDevice_t *busDev, unsigned char reg, unsigned char *values)
{
  return busReadBuf(busDev, reg, values, 1);
}
char busWrite(busDevice_t *busDev, unsigned char reg, unsigned char value)
{
  unsigned char values[2] = {reg, value};
  return busWriteBuf(busDev, reg, values, 2);
}




void myprint(uint64_t value)
{
  const int NUM_DIGITS    = log10(value) + 1;

  char sz[NUM_DIGITS + 1];

  sz[NUM_DIGITS] =  0;
  for ( size_t i = NUM_DIGITS; i--; value /= 10)
  {
    sz[i] = '0' + (value % 10);
  }

  Serial1.print(sz);
}
void myprintln(uint64_t value)
{
  myprint(value);
  Serial1.println("");
}



#define SPL06_I2C_ADDR                         0x76
#define SPL06_DEFAULT_CHIP_ID                  0x10

#define SPL06_PRESSURE_START_REG               0x00
#define SPL06_PRESSURE_LEN                     3       // 24 bits, 3 bytes
#define SPL06_PRESSURE_B2_REG                  0x00    // Pressure MSB Register
#define SPL06_PRESSURE_B1_REG                  0x01    // Pressure middle byte Register
#define SPL06_PRESSURE_B0_REG                  0x02    // Pressure LSB Register
#define SPL06_TEMPERATURE_START_REG            0x03
#define SPL06_TEMPERATURE_LEN                  3       // 24 bits, 3 bytes
#define SPL06_TEMPERATURE_B2_REG               0x03    // Temperature MSB Register
#define SPL06_TEMPERATURE_B1_REG               0x04    // Temperature middle byte Register
#define SPL06_TEMPERATURE_B0_REG               0x05    // Temperature LSB Register
#define SPL06_PRESSURE_CFG_REG                 0x06    // Pressure config
#define SPL06_TEMPERATURE_CFG_REG              0x07    // Temperature config
#define SPL06_MODE_AND_STATUS_REG              0x08    // Mode and status
#define SPL06_INT_AND_FIFO_CFG_REG             0x09    // Interrupt and FIFO config
#define SPL06_INT_STATUS_REG                   0x0A    // Interrupt and FIFO config
#define SPL06_FIFO_STATUS_REG                  0x0B    // Interrupt and FIFO config
#define SPL06_RST_REG                          0x0C    // Softreset Register
#define SPL06_CHIP_ID_REG                      0x0D    // Chip ID Register
#define SPL06_CALIB_COEFFS_START               0x10
#define SPL06_CALIB_COEFFS_END                 0x21

#define SPL06_CALIB_COEFFS_LEN                 (SPL06_CALIB_COEFFS_END - SPL06_CALIB_COEFFS_START + 1)

// TEMPERATURE_CFG_REG
#define SPL06_TEMP_USE_EXT_SENSOR              (1<<7)

// MODE_AND_STATUS_REG
#define SPL06_MEAS_PRESSURE                    (1<<0)  // measure pressure
#define SPL06_MEAS_TEMPERATURE                 (1<<1)  // measure temperature

#define SPL06_MEAS_CFG_CONTINUOUS              (1<<2)
#define SPL06_MEAS_CFG_PRESSURE_RDY            (1<<4)
#define SPL06_MEAS_CFG_TEMPERATURE_RDY         (1<<5)
#define SPL06_MEAS_CFG_SENSOR_RDY              (1<<6)
#define SPL06_MEAS_CFG_COEFFS_RDY              (1<<7)

// INT_AND_FIFO_CFG_REG
#define SPL06_PRESSURE_RESULT_BIT_SHIFT        (1<<2)  // necessary for pressure oversampling > 8
#define SPL06_TEMPERATURE_RESULT_BIT_SHIFT     (1<<3)  // necessary for temperature oversampling > 8

// TMP_RATE (Background mode only)
#define SPL06_SAMPLE_RATE_1   0
#define SPL06_SAMPLE_RATE_2   1
#define SPL06_SAMPLE_RATE_4   2
#define SPL06_SAMPLE_RATE_8   3
#define SPL06_SAMPLE_RATE_16  4
#define SPL06_SAMPLE_RATE_32  5
#define SPL06_SAMPLE_RATE_64  6
#define SPL06_SAMPLE_RATE_128 7

// See datasheet Table 9
#define SPL06_PRESSURE_SAMPLING_RATE     SPL06_SAMPLE_RATE_16
#define SPL06_PRESSURE_OVERSAMPLING            32
#define SPL06_TEMPERATURE_SAMPLING_RATE     SPL06_SAMPLE_RATE_1
#define SPL06_TEMPERATURE_OVERSAMPLING         1

#define SPL06_MEASUREMENT_TIME(oversampling)   ((2 + lrintf(oversampling * 1.6)) + 1) // ms





int8_t spl06_samples_to_cfg_reg_value(uint8_t sample_rate)
{
  switch (sample_rate)
  {
    case 1: return 0;
    case 2: return 1;
    case 4: return 2;
    case 8: return 3;
    case 16: return 4;
    case 32: return 5;
    case 64: return 6;
    case 128: return 7;
    default: return -1; // invalid
  }
}

int32_t spl06_raw_value_scale_factor(uint8_t oversampling_rate)
{
  switch (oversampling_rate)
  {
    case 1: return 524288;
    case 2: return 1572864;
    case 4: return 3670016;
    case 8: return 7864320;
    case 16: return 253952;
    case 32: return 516096;
    case 64: return 1040384;
    case 128: return 2088960;
    default: return -1; // invalid
  }
}




bool spl06_read_temperature(baroDev_t * baro)
{
  uint8_t data[SPL06_TEMPERATURE_LEN];
  int32_t spl06_temperature;

  bool ack = busReadBuf(baro->busDev, SPL06_TEMPERATURE_START_REG, data, SPL06_TEMPERATURE_LEN);

  if (ack) {
    spl06_temperature = (int32_t)((data[0] & 0x80 ? 0xFF000000 : 0) | (((uint32_t)(data[0])) << 16) | (((uint32_t)(data[1])) << 8) | ((uint32_t)data[2]));
    baro->spl06_temperature_raw = spl06_temperature;
  }

  return ack;
}

bool spl06_read_pressure(baroDev_t * baro)
{
  uint8_t data[SPL06_PRESSURE_LEN];
  int32_t spl06_pressure;

  bool ack = busReadBuf(baro->busDev, SPL06_PRESSURE_START_REG, data, SPL06_PRESSURE_LEN);

  if (ack) {
    spl06_pressure = (int32_t)((data[0] & 0x80 ? 0xFF000000 : 0) | (((uint32_t)(data[0])) << 16) | (((uint32_t)(data[1])) << 8) | ((uint32_t)data[2]));
    baro->spl06_pressure_raw = spl06_pressure;
  }

  return ack;
}

// Returns temperature in degrees centigrade
float spl06_compensate_temperature(baroDev_t * baro, int32_t temperature_raw)
{
  const float t_raw_sc = (float)temperature_raw / spl06_raw_value_scale_factor(SPL06_TEMPERATURE_OVERSAMPLING);
  const float temp_comp = (float)baro->spl06_cal.c0 / 2 + t_raw_sc * baro->spl06_cal.c1;
  return temp_comp;
}
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

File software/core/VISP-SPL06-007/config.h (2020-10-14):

/*
   This file is part of VISP Core.

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
   Author: Steven.Carr@hammontonmakers.org
*/

#ifndef __MY_CONFIG_H__
#define __MY_CONFIG_H__
#include <stdarg.h>
#include <stdint.h>

#ifdef ARDUINO_TEENSY40
#include "teensy.h"
#elif ARDUINO_BLUEPILL_F103C8
#include "bluepill.h"
#elif ARDUINO_AVR_NANO
#include "nano.h"
#elif ARDUINO_AVR_UNO
#include "nano.h"
#define WANT_BMP388 1 // 1858 bytes and 112bytes of ram, fits on the UNO but not the Nano right now
#else
#error Unsupported board selection.
#endif

// Don't compile this function inline
//   '__NOINLINE void foo(void){ ... }'
#ifdef __GNUC__
#define __NOINLINE  __attribute__ ((noinline))
#else
#define __NOINLINE error 'NOINLINE' not defined for this compiler
#endif

#define SERIAL_BAUD 112500

// Battery level resistor divider located on the carrier board
#define B_DIV_R1 100 // K
#define B_DIV_R2 22  // K
  
// System modes (This needs to be a bitmask friendly for settings validity checking (setting Volume when in Pressure mode is an error)
#define MODE_NONE  0x00
#define MODE_OFF   0x01
#define MODE_PCCMV 0x02
#define MODE_VCCMV 0x04
#define MODE_MANUAL_PCCMV 0x20 // By ADC input
#define MODE_MANUAL_VCCMV 0x40 // By ADC input
#define MODE_ALL   0xFF
#define MODE_MANUAL (MODE_MANUAL_PCCMV|MODE_MANUAL_VCCMV) // Used to disable things from a display interface if the ADC input is turned to a setting
// rate, i:e, pressure, volume, mode as analog inputs  5 of them...  e have 6 available on the nano!

// We can always add an I2C ADC chip for more input capability (couple bucks)

extern uint8_t currentMode;

typedef enum {
  DEBUG_DISABLED = 0,
  DEBUG_ENABLED
} debugState_e;

extern debugState_e debug;

#define MIN_BREATH_RATIO 2
#define MAX_BREATH_RATIO 5
#define MIN_BREATH_RATE  10 // TODO: saner limits 5 breaths/minute
#define MAX_BREATH_RATE  40 // TODO: saner limits 30 breaths/minute
#define MIN_BREATH_PRESSURE 0    // TODO: saner limits
#define MAX_BREATH_PRESSURE 80  // TODO: saner limits
#define MIN_BREATH_VOLUME   0    // TODO: saner limits 
#define MAX_BREATH_VOLUME   800 // TODO: saner limits

void clearCalibrationData();

extern uint16_t breathPressure; // For pressure controlled automatic ventilation
extern uint16_t breathVolume;
extern uint8_t breathRate;
extern uint8_t breathRatio;
extern uint16_t breathThreshold;
extern int8_t batteryLevel;
extern int8_t FiO2Level;
extern volatile unsigned long timeToIgnoreHome;

#define VERSION_MAJOR     0
#define VERSION_MINOR     1
#define VERSION_REVISION  7


// Motor specific configurations

// percentage as 0->100 of MAX_PWM
#define HBRIDGE_SWEEP_SPEED   65 // Ford F150 motor wiper
#define STEPPER_SWEEP_SPEED   50

#define MOTOR_ENCODER_FEEDBACK   MOTOR_PIN_A  // Must be IRQ capable

// ok, we can have a simple H bridge  HiLetGo BTS7960
#define MOTOR_HBRIDGE_R_EN    MOTOR_PIN_B   // R_EN: forware drive enable input, high-level enable, low level off  (ACTIVE_HIGH)
#define MOTOR_HBRIDGE_L_EN    MOTOR_PIN_C   // L_EN: Reverse drive enable input, high-level enable, low level off  (ACTIVE HIGH)
#define MOTOR_HBRIDGE_PWM     MOTOR_PIN_PWM // PWM: PWM signal, active high, attach to BOTH LPWM and RPWM
// WARNING: If you enable R_EN and L_EN at the same time, you fry the chip, so always set both to 0 first, then enable delay(1) and then set the direction pin
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

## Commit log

2020-03-25 initial upload
    [arm.stl, bag_mount.stl, base_b.stl, base_t.stl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]
2020-03-25 moved stuff to allow software
    [arm.stl, bag_mount.stl, base_b.stl, base_t.stl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]
2020-03-25 labeled stuff
    [cosv.scad]
2020-03-25 smaller body, less bolts
    [cosv.scad]
2020-03-25 softened base corner, rendered for bldc
    [base_b.stl, base_b_bldc.stl, cosv.scad]
2020-03-25 updates for laser, some output renders
    [base_t.stl, cosv.scad]
2020-03-25 renamed output to rendered
    [arm.stl, bag_mount.stl, base_b_bldc.stl, base_t.stl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]
2020-03-25 changes for rendering laser files
    [arm.stl, cam.stl, cosv.scad]
2020-03-25 bldc motor standoff
    [bldc_motor_standoff.stl, cosv.scad]
2020-03-25 more laser parts
    [cosv.scad]
2020-03-25 more rendered output files
    [cam.stl, cam_6.35mm.stl, cam_6mm.stl, cam_8mm.stl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]
2020-03-25 more renders
    [bldc_motor_standoff.stl, cosv.scad]
2020-03-27 FFF cam was too short since exploding
    [cam_6.35mm.stl, cam_6mm.stl, cam_8mm.stl, cosv.scad]
2020-03-28 created flow sensor for baro sensors pcb
    [cosv.scad, flow_sensor_for_pcb.stl]
2020-03-28 new arms for milling from plywood
    [arm_thick.stl, cosv.scad]
2020-03-28 ports didn't go through
    [cosv.scad, flow_sensor_for_pcb.stl]
2020-03-29 updates for cover and chips of sensor
    [cosv.scad, flow_sensor_for_pcb.stl]
2020-03-29 renders for milling
    [base_b_bldc.stl, base_b_gear.stl, base_b_nema23.stl, cosv.scad]
2020-03-30 flow sensor body done!
    [cosv.scad, flow_sensor_cover.stl]
2020-03-30 projection to check port placement
    [cosv.scad]
2020-03-30 fixed path for pitot, cover work
    [cosv.scad, flow_sensor_cover.stl, flow_sensor_cover_oled.stl]
2020-03-31 rendered the paddles
    [cosv.scad, paddle_large.stl, paddle_small.stl]
2020-03-31 SLA version with no bevel
    [cosv.scad]
2020-04-02 tube size adjustment, cover h and oled pins
    [cosv.scad, flow_sensor_cover.stl, flow_sensor_cover_oled.stl]
2020-04-05 Added software, commented source, flow_test part
    [cosv.scad, flow_test.stl]
2020-04-05 VISP pcb files
    [sensors.brd, sensors.sch]
2020-04-05 clipped version for oversize test PCB
    [cosv.scad]
2020-04-08 reworked laser files
    [cosv.scad]
2020-04-08 laser washers and paddle name
    [cosv.scad]
2020-04-10 pcb now 20mm wide
    [cosv.scad, flow_sensor_cover.stl, flow_sensor_cover_oled.stl]
2020-04-15 rendered FFF for threaded rod/thicker arm
    [arm.stl, bag_mount.stl, base_b_bldc.stl, base_b_nema.stl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]
2020-04-15 other format test
    [cam_12mm_double_d.amf, cosv.scad]
2020-04-15 linefeed test
    [cam_12mm_double_d.stl]
2020-04-16 re-rendered to ensure these are up to date
    [cosv.scad]
2020-04-23 renders for 0.2 kerf, start on display
    [bag_mount.stl, base_b_nema.dxf, cosv.scad, fan_callibration_adapter.stl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]
2020-04-24 power supply mount and UI updates
    [cosv.scad, supply_cover.stl]
2020-04-27 core testing work + UI
    [cosv.scad, flow_sensor_cover.stl, flow_sensor_cover_oled.stl, supply_cover_38x98.stl]
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2020-04-28 UI integration work
    [cosv.scad]
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2020-05-02 new laser arms
    [cosv.scad, laser_arm.dxf]
2020-05-02 milling arm
    [cosv.scad, mill_arm.stl]
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2020-05-04 Automate the generation of STL, SVG, and DXF files
    [cosv.scad]
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2020-05-04 new paddle
    [cosv.scad, paddle_new.stl]
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2020-05-05 Generate all cam and base plate types for the different motors available Also, make the scad file thingiverse compatible for customization
    [cosv.scad]
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2020-05-10 Massive changes to body. Tab/slot assembly.
    [arm_mount.dxf, base_b_nema.dxf, base_mount_bottom.dxf, base_mount_top.dxf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]
2020-05-10 More non cut parts in physical form for clearance.
    [cosv.scad]
2020-05-10 HELP ME PICK AN OSHW LICENSE. Please.
    [cosv.scad]
2020-05-10 And.. one word missing changes the whole meaning.
    [cosv.scad]
2020-05-10 Laser files and paddle rendered
    [arm.stl, arm_mount.dxf, arm_thick.stl, bag_mount.stl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]
2020-05-10 less material paddle
    [cosv.scad, paddle.stl]
2020-05-11 led hole correction, new renders
    [cosv.scad, laser_base_bottom.dxf, laser_base_front.dxf, laser_base_top.dxf]
2020-05-11 Motor model was 7mm off, moved H-bridge.
    [cosv.scad, laser_base_end_bottom_cap.dxf, laser_base_end_top_cap.dxf, laser_base_mount_bottom.dxf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]
2020-05-11 Actually render the changes..
    [cosv.scad, laser_base_back.dxf]
2020-05-11 Actually render the files, again.
    [cosv.scad, laser_base_end_top_cap.dxf]
2020-05-11 moved the motor cutout the wrong way..
    [cosv.scad, laser_base_back.dxf]
2020-05-11 Front panel for FFF
    [base_front.stl, cosv.scad]
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2020-05-12 cam encoder
    [cosv.scad]
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2020-05-12 pi front panel
    [cam_encoder.stl, cosv.scad, laser_base_front_pi_layer_0.dxf, laser_base_front_pi_layer_1.dxf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]
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2020-05-15 dimension tweaks, removable front/back, encoder
    [cosv2.scad, laser_base_back.dxf, laser_base_back_wiper.dxf, laser_base_front.dxf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]
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2020-05-16 dimension tweaks
    [cosv.scad, laser_arm_mount_motor.dxf, laser_base_mount_left.dxf, laser_bearing_bushing_4x8.dxf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]
2020-05-18 centered home, encoder with through nuts
    [cosv.scad, laser_base_mount_left.dxf, laser_cam_center_6mm.dxf, laser_cam_encoder.dxf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]
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2020-05-24 battery mounts, encoder tweaks
    [cosv.scad, laser_arm_mount.dxf, laser_arm_mount_motor.dxf, laser_base_battery_mount_b.dxf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]
2020-05-24 laser files cleanup
    [cosv.scad, laser_base_end_top.dxf, laser_bearing_bushing_4mm.dxf, laser_bearing_bushing_4x8mm.dxf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]
2020-05-24 kerf tester strip
    [cosv.scad, laser_bearing_kerf_test.dxf]
2020-05-24 rendered for kerf 0.04
    [cosv.scad, laser_arm.dxf, laser_arm_end_support.dxf, laser_arm_mount.dxf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]
2020-05-24 generated wrong item
    [cosv.scad, laser_base_end_right_inner.dxf]
2020-05-24 Automate the generation of DXF and SVG files for future automated panelization
    [cosv.scad]
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2020-05-27 Update I2C MUX board for VISP. Now, it can support a sensor on every pad (for direct comparison analysis) Lowered I2C pullup values. Each sensor is on it's own I2C bus behind the MUX Wire pads have b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
    [sensors.brd, sensors.sch]
2020-05-27 New TEENSY 4.0 carrier board for COSV Supports both analog+2.8" SPI display and rPi interfaces Also, supports rPi only mode of operation with solder jumper (sans battery level monitoring)
    [cosv-carrier-teensy40.brd, cosv-carrier-teensy40.sch]
2020-05-28 Make the motor connector identical to the Arduino IBT_2 H-Bridge
    [cosv-carrier-teensy40.brd, cosv-carrier-teensy40.sch]
2020-05-28 Add second I2C channel to VISP connector
    [cosv-carrier-teensy40.brd, cosv-carrier-teensy40.sch]
2020-05-28 dir cleanup
    [cosv.scad, kerf_slot_test.dxf, laser_arm.dxf, laser_arm_end_support.dxf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]
2020-05-28 Add Line Power Detect input and Watchdog Pulse output for alarm subsystem
    [cosv-carrier-teensy40.brd, cosv-carrier-teensy40.sch]
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2020-06-15 Add Photo Interrupter Board for COSV
    [PhotoInterrupter.brd, PhotoInterrupter.sch]
2020-06-15 Round the corners a bit more to keep from getting hit by the cam arm
    [PhotoInterrupter.brd]
2020-06-22 JLCPCB Proven - Dual I2C board with BMP280/SLP06-007 footprints
    [assembly.csv, sensors.brd, sensors.sch, sensorsBOM-BMP280.csv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]
2020-06-22 Snap In Photo Interrupter Enhancements.
    [PhotoInterrupter.brd, PhotoInterrupter.sch]
2020-06-22 Label parts properly HY870-L and EE-SX1042 components
    [PhotoInterrupter.brd, PhotoInterrupter.sch]
2020-07-04 New "millable" Carrier board for use with rPI3+ on COSV
    [cosv-carrier-teensy40.brd, cosv-carrier-teensy40.sch]
2020-07-04 Clean up part/pin names on board
    [cosv-carrier-teensy40.brd]
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2020-08-24 New! Teensy 4.0 Carrier board with analog support This bord supports standalone mode using analog pots to control everything.
    [cosv-carrier-teensy40.brd, cosv-carrier-teensy40.sch]
2020-08-25 Update VISP-I2C-MUX for manufacturing by OSH-Park All 8 sensor pads can be populated simultaneously without I2C bus conflicts. Updated board text to reflect new capabilities Increased width slightly 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
    [sensors.brd, sensors.sch]
2020-08-25 Routed for easier milling
    [cosv-carrier-teensy40_2.brd, cosv-carrier-teensy40_2.sch]
2020-08-25 v7 export
    [cosv-carrier-teensy40_v7.brd, cosv-carrier-teensy40_v7.sch]
2020-09-01 Enlarge labels to make them readable by humans on the VISP-I2C-MUX PCB
    [sensors.brd]
2020-09-01 Update Label: Pullup resistors are 2K7 on the downstream I2C buses
    [sensors.brd]
2020-09-04 Add version V0.2 to the VISP PCB
    [sensors.brd]
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2020-09-18 New BMP388-only I2C MUX board, the latest (and greatest) board for the VISP.
    Now, each of the 4 sensors are on separate I2C buses.
    [visp-i2c-mux-bmp388-bom.csv, visp-i2c-mux-bmp388.brd, visp-i2c-mux-bmp388.sch]
2020-09-18 Remove non-supported VISP boards
    [sensors.brd, sensors.sch]
2020-09-22 Update notes in schematics for VISP PCB's
    [sensors.sch, visp-i2c-mux-bmp388.sch]
2020-09-29 Add eagle 9.6.2 version of visp for board manufacturing
    [visp-i2c-mux-bmp388-eagle-962.brd, visp-i2c-mux-bmp388-eagle-962.sch]
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

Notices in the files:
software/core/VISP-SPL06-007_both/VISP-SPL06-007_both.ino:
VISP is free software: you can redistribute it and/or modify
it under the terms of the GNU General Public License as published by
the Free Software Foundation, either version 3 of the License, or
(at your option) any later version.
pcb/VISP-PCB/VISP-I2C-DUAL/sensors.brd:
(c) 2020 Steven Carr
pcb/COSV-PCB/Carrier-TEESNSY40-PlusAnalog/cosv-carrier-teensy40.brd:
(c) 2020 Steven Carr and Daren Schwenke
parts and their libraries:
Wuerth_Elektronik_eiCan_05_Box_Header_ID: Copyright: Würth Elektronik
